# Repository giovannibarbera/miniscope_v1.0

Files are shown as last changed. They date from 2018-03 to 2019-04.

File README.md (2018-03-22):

# MiniScope v1.0 - First generation miniature epifluorescence microscope

This repository contains the design files, software and scripts for fabrication and use of the first generation miniature epifluorescence microscope used in [1] and [2].

## Table of content

[MATLAB-data-analysis](./MATLAB-data-analysis/) - Matlab scripts for image processing/calcium traces extraction

[NeuView](./NeuView/) - Data acquisition software

[PCB-DAQ](./PCB-DAQ/) - Data acquisition PCB design (gerber) files

[PCB-miniscope](./PCB-miniscope/) - MiniScope PCB design (gerber) files

[STL-DAQ](./PCB-miniscope/) - Data acquisition system box

[STL-miniscope](./STL-miniscope/) - MiniScope mechanical design

## References

[1] G. Barbera, B. Liang, L. Zhang, C. R. Gerfen, E. Culurciello, R. Chen, Y. Li, D. Lin. *“Spatially Compact Neural Clusters in the Dorsal Striatum Encode Locomotion Relevant Information”*, Neuron **92**: 1-12, 2016.

[2] L. Zhang, B. Liang, G. Barbera, S. Hawes, Y. Zhang, K. Stump, I. Baum, Y. Yang, Y. Li, D. Lin. *“Miniscope GRIN lens system for calcium imaging of neuronal activity of deep brain structures in behaving animals”*, under review.

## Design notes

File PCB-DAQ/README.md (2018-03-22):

# Data acquisition board design files

The data acquisition system includes:

[CONN_board](../PCB-DAQ/CONN_board/) - Connector board

[DAQ_main_board](../PCB-DAQ/DAQ_main_board/) - Main data acquisition board

[LED_board](../PCB-DAQ/LED_board/) - Indicator LED board

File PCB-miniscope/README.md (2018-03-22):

# MiniScope PCB design files

These are the gerber files for the miniScope PCB. 
Use the text file PCB_specs_MINISCOPE.docx as a reference for the board specification when ordering.

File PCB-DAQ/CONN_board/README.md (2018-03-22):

# DAQ connector board design files

These are the gerber files for the data acquisition connector board. Use the text file PCB_specs_CONN.docx as a reference for the board specification and CONN (Component positions).csv as a placement file when ordering.

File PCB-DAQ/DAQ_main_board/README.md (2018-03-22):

# Data acquisition board design files

These are the gerber files for the data acquisition system. Use the text file PCB_specs_DAQ.docx as a reference for the board specification and DAQ (Component positions).csv as a placement file when ordering.
This DAQ supports dual LED and is wi-fi ready through the TI CC3000 module.

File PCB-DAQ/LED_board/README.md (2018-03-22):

# LED indicator board design files

These are the gerber files for the data acquisition LED indicator board. Use the text file PCB_specs_LED.docx as a reference for the board specification and LED (Component positions).csv as a placement file when ordering.

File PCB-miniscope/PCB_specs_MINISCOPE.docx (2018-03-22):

# PCB specifications for MiniScope v1.0 image sensor board

# Layer order:

1 - Top

Inner 2 - VDD3V3 Plane (POWER)

Inner 3 - DGND Plane (GROUND)

4 - Bottom

# Gerber files description:

# Board Outline: MINISCOPE - Board Outline.gbr

# Bottom Solder Paste: MINISCOPE - Bottom Copper (Paste).gbr

# Bottom Layer: MINISCOPE - Bottom Copper.gbr

Inner Layer 2: MINISCOPE - VDD_3V3 Plane (Powerplane).gbr

Drills: MINISCOPE - Drill Data - [Through Hole].drl

Top Solder Paste: MINISCOPE - Top Copper (Paste).gbr

Top Layer: MINISCOPE - Top Copper.gbr

Top Silkscreen: MINISCOPE - Top Silkscreen.gbr

Bottom Silkscreen: MINISCOPE - Bottom Silkscreen.gbr

Inner Layer 3: MINISCOPE - DGND Plane (Powerplane).gbr

# PCB specifications:

# Layers: 4

PCB Fabrication Spec (IPC Spec): IPC-600G Class 2

Material: Nan Ya NP-175

Finished Thickness: 0.031 inches

Thickness Tolerance: Plus or Minus 10%

Surface Finish: ENIG/HASL

Surface Finish 2: None

Gold Fingers: No

Outer Layer Finish Copper: 1 Oz

Inner Copper: 1 Oz Inners

Flex Board: No

ITAR: No

Board Dimensions: 0.4405 in x 0.4115 in

Route and Retain: No

Scoring : No

ROHS compliant: No

Edge Plating: No

Minimum Hole Size: 19.7 Mils

Minimum Annular Ring Width (Component Holes): 8 mil or more

Internal Slots: None

Internal Cutouts: None

Counter Sink: No

Counter Bore: No

Edge Plated Holes: No

Min Trace (Outer layer): 6 mils

Min Space (Outer layer): 5 mils

Min Trace (Inner layer): 6 mils

Min Space (Inner layer): 5 mils

Solder Mask Sides: Top and Bottom

Solder Mask Via Opens: Covered on both sides

Silk Screen Sides: Both

Thru-Hole Via in Pad: Yes

Thru-Hole Filled Via: Non-Conductive

SM Plugged Vias: No

Minimum Drill to Copper distance: 0.0081 inches

Blind vias: No

Buried vias: No

Controlled depth drilling: No

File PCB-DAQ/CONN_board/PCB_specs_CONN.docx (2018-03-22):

# PCB specifications for MiniScope v1.0 DAQ connector board

# Layer order:

1 - Top

Inner 2 - DGND Plane (GROUND)

Inner 3 - VDD3V3 Plane (POWER)

4 - Bottom

# Gerber files description:

# Board Outline: CONN - Board Outline.gbr

# Bottom Solder Paste: CONN - Bottom Copper (Paste).gbr

# Bottom Solder Mask CONN - Bottom Copper (Resist).gbr

# Bottom Layer: CONN - Bottom Copper.gbr

Bottom Silkscreen: CONN - Bottom Silkscreen.gbr

Inner Layer 2: CONN - DGND Plane (Powerplane).gbr

Drills: CONN - Drill Data - [Through Hole].drl

Top Solder Paste: CONN - Top Copper (Paste).gbr

# Top Solder Mask CONN - Top Copper (Resist).gbr

Top Layer: CONN - Top Copper.gbr

Top Silkscreen: CONN - Top Silkscreen.gbr

Inner Layer 3: CONN - VDD_3V3 Plane (Powerplane).gbr

# PCB specifications:

# Layers: 4

ITAR: no

Certs: IPC Class 2-A600

AS9100: no

Electrical Test: no

5% OVERAGE: no

Material Type: FR4

Material Thickness: 0.062"

Board Finish: LFSolder

Unit Dimensions: 2.2 in x 0.4 in

Tab Rout: no

Scoring: no

Copper Weight: 1 oz

Inner Copper Weight: 1.0

Solder Mask Sides: Both Sides

Solder Mask Color: Green

Legend Silk Scrn: Both Sides

Legd/Silk Scrn Color: White

Castellated Holes: no

Blind/Buried Vias: None

SM Plugged Via: no

Via-In-Pad: None

Microvias: None

Plated Slots: no

Plated Edges: no

CounterSinks: no

CounterBores: no

CtrSinksPlated: 0

CtrBoresPlated: 0

CtrSinksNon-Pltd: 0

CtrBoresNon-Pltd: 0

Ctrld Dielectric: no

Ctrld Impedance: no

Etchback: no

# Pem Nuts: 0

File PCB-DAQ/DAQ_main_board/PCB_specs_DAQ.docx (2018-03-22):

# PCB specifications for MiniScope v1.0 data acquisition board

# Layer order:

1 - Top

Inner 2 - DGND Plane (GROUND)

Inner 3 - VDD3V3 Plane (POWER)

4 - Bottom

# Gerber files description:

# Board Outline: DAQ - Board Outline.gbr

# Bottom Solder Paste: DAQ - Bottom Copper (Paste).gbr

# Bottom Solder Mask DAQ - Bottom Copper (Resist).gbr

# Bottom Layer: DAQ - Bottom Copper.gbr

Bottom Silkscreen: DAQ - Bottom Silkscreen.gbr

Inner Layer 2: DAQ - DGND Plane (Powerplane).gbr

Drills: DAQ - Drill Data - [Through Hole].drl

Top Solder Paste: DAQ - Top Copper (Paste).gbr

# Top Solder Mask DAQ - Top Copper (Resist).gbr

Top Layer: DAQ - Top Copper.gbr

Top Silkscreen: DAQ - Top Silkscreen.gbr

Inner Layer 3: DAQ - VDD_3V3 Plane (Powerplane).gbr

# PCB specifications:

# Layers: 4

ITAR: no

Certs: IPC Class 2-A600

AS9100: no

Electrical Test: no

5% OVERAGE: no

Material Type: FR4

Material Thickness: 0.062"

Board Finish: LFSolder

Unit Dimensions: 2.3 in x 2.1 in

Tab Rout: no

Scoring: no

Copper Weight: 1 oz

Inner Copper Weight: 1.0

Solder Mask Sides: Both Sides

Solder Mask Color: Green

Legend Silk Scrn: Both Sides

Legd/Silk Scrn Color: White

Castellated Holes: no

Blind/Buried Vias: None

SM Plugged Via: no

Via-In-Pad: None

Microvias: None

Plated Slots: no

Plated Edges: no

CounterSinks: no

CounterBores: no

CtrSinksPlated: 0

CtrBoresPlated: 0

CtrSinksNon-Pltd: 0

CtrBoresNon-Pltd: 0

Ctrld Dielectric: no

Ctrld Impedance: no

Etchback: no

# Pem Nuts: 0

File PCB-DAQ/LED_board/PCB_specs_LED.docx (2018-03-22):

# PCB specifications for MiniScope v1.0 DAQ LED board

# Layer order:

1 - Top

Inner 2 - DGND Plane (GROUND)

Inner 3 - DGND Plane2 (GROUND)

4 - Bottom

# Gerber files description:

# Board Outline: LED - Board Outline.gbr

# Bottom Solder Paste: LED - Bottom Copper (Paste).gbr

# Bottom Solder Mask LED - Bottom Copper (Resist).gbr

# Bottom Layer: LED - Bottom Copper.gbr

Bottom Silkscreen: LED - Bottom Silkscreen.gbr

Inner Layer 2: LED - DGND Plane (Powerplane).gbr

Inner Layer 3: LED - DGND Plane2 (Powerplane).gbr

Drills: LED - Drill Data - [Through Hole].drl

Top Solder Paste: LED - Top Copper (Paste).gbr

# Top Solder Mask LED - Top Copper (Resist).gbr

Top Layer: LED - Top Copper.gbr

Top Silkscreen: LED - Top Silkscreen.gbr

Inner Layer 3: LED - VDD_3V3 Plane (Powerplane).gbr

# PCB specifications:

# Layers: 4

ITAR: no

Certs: IPC Class 2-A600

AS9100: no

Electrical Test: no

5% OVERAGE: no

Material Type: FR4

Material Thickness: 0.062"

Board Finish: LFSolder

Unit Dimensions: 0.95 in x 0.36 in

Tab Rout: no

Scoring: no

Copper Weight: 1 oz

Inner Copper Weight: 1.0

Solder Mask Sides: Both Sides

Solder Mask Color: Green

Legend Silk Scrn: Both Sides

Legd/Silk Scrn Color: White

Castellated Holes: no

Blind/Buried Vias: None

SM Plugged Via: no

Via-In-Pad: None

Microvias: None

Plated Slots: no

Plated Edges: no

CounterSinks: no

CounterBores: no

CtrSinksPlated: 0

CtrBoresPlated: 0

CtrSinksNon-Pltd: 0

CtrBoresNon-Pltd: 0

Ctrld Dielectric: no

Ctrld Impedance: no

Etchback: no

# Pem Nuts: 0

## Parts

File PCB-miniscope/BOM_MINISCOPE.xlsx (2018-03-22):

Description | QTY | Ref Des | Manufacturer | Manufacturer PN | Distributor | Distributor PN | Unit price | Ext. price
Ferrite Chip 120Ohm 60mA 0603 | 2 | FERR, FERR1 | TDK | MMZ1608B121C | Digikey | 445-2164-1-ND | $0.100 | $0.200
Cap Cer 1000pF 6.3V X5R 01005 | 1 | C4 | TDK | C0402X5R0J102K020BC | Digikey | 445-5509-1-ND | $0.240 | $0.240
Cap Cer 10000pF 6.3V X5R 01005 | 2 | C6, C12 | TDK | C0402X5R0J103K020BC | Digikey | 445-5515-1-ND | $0.250 | $0.500
Cap Cer 0.1uF 4V 20% X5R 01005 | 3 | C3, C7, C13 | TDK | C0402X5R0G104M020BC | Digikey | 445-8916-1-ND | $0.390 | $1.170
Cap Cer 1uF 6.3V 20% X5R 0201 | 3 | C2, C9, C10 | TDK | C0603X5R0J105M030BC | Digikey | 445-8008-1-ND | $0.370 | $1.110
Cap Cer 10uF 6.3V 20% X5R 0J106 | 3 | C1, C5, C11 | TDK | C1005X5R0J106M050BC | Digikey | 445-8920-1-ND | $0.610 | $1.830
Cap Cer 22uF 6.3V 20% X5R0805 | 1 | C8 | TDK | C2012X5R0J226M125AC | Digikey | 445-1422-1-ND | $0.290 | $0.290
Res 1K OHM 1/32W 5% 01005 SMD | 2 | R1, R2 | Panasonic | ERJ-XGNJ102Y | Digikey | P1.0KAWCT-ND | $0.590 | $1.180
Res 1.5K OHM 1/32W 5% 01005 SMD | 2 | R3, R4 | Panasonic | ERJ-XGNJ152Y | Digikey | P1.5KAWCT-ND | $0.590 | $1.180
Res 220 OHM 1/32W 5% 01005 SMD | 1 | R5 | Panasonic | ERJ-XGNJ221Y | Digikey | P220AWCT-ND | $0.590 | $0.590
IC REG LDO 3.3V 0.5A TSOT23-5 | 1 | ADP1710_3V3 | ON Semiconductors | CAT6219-330TDGT3 | Digikey | CAT6219-330TDGT3CT-ND | $0.970 | $0.970
Polarized Nano Connector PZN-10-VV | 1 | U$1 | Omnetics | A79617-001 | Omnetics | A79617-001 | $27.720 | $27.720
Image Sensor Monochrome CMOS 52-Pin IBGA | 1 | MT9V022 | Aptina | MT9V022IA7ATM | Arrow | MT9V022IA7ATM | $19.070 | $19.070
Tot. |  |  |  |  |  |  |  | $56.050

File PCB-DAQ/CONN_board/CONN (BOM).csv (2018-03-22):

Ref Name | Qty | Component | Value | Side | Manufacturer | Manufacturer part number | Distributor | Distributor part number | Description | Price | Ext price
TRIG LED | 2 | CONN2_THROUGH_2MM |  | Top | Harwin | M80-8520242 | Digikey | 952-1769-ND | 02 SIL MALE CONNECTOR | 1.19 | 2.38
CONN10 | 1 | CONN10_THROUGH_2MM |  | Top | Harwin | M80-8691022 | Digikey | 952-2405-5-ND | CONN HDR 2MM VERT DUAL 10POS | 2.67 | 2.67
CONN25 | 1 | CONN25_FLAT_2013928-8 |  | Bottom | TE Connectivity | 2013928-8 | Digikey | A100213CT-ND | CONN FPC 25POS .3MM FLIP LOC SMD | 1.27 | 1.27
OMNV10 | 1 | OMNETICS_PNZ_10_VV_SMT |  | Top | Omnetics | A79617-001 | Omnetics | A79617-001 | OMNETICS PZN-10-VV | 29 | 29
 |  |  |  |  |  |  |  |  |  | Tot. | 35.32

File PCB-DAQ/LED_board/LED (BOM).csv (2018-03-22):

Ref Name | Qty | Component | Value | Side | Manufacturer | Manufacturer part number | Distributor | Distributor part number | Description | Price | Ext price
LED1 | 1 | LED_GREEN_0805 |  | Top | Lite-On | LTST-C171GKT | Digikey | 160-1423-1-ND | LED GREEN CLEAR THIN 0805 SMD | 0.3 | 0.3
LED2 LED3 LED4 | 3 | LED_BLUE_0805 |  | Top | Lite-On | LTST-C171TBKT | Digikey | 160-1645-1-ND | LED 468NM BLUE CLEAR 0805 SMD | 0.44 | 1.32
U1 | 1 | Molex_0908140906 |  | Bottom | Molex | 908140906 | Digikey | WM3638CT-ND | CONN HEADER 6POS 1.27MM VERT SMD | 1.16 | 1.16
 |  |  |  |  |  |  |  |  |  | Tot. | 2.78

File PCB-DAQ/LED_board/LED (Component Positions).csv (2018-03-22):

Name | Component | Side | Centre X | Centre Y | Rotation
LED2 | LED_BLUE_0805 | Top | 1.72 | -3.46 | 0.00
LED3 | LED_BLUE_0805 | Top | 14.72 | -3.46 | 0.00
LED4 | LED_BLUE_0805 | Top | 21.22 | -3.46 | 0.00
LED1 | LED_GREEN_0805 | Top | 8.22 | -3.46 | 0.00
U1 | Molex_0908140906 | Bottom | 11.78 | -4.51 | 0.00

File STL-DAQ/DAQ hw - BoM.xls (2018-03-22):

DAQ hardware for MiniScope v1.0
Ref Name | Qty | Component | Value | Layer | Manufacturer | Manufacturer PN | Distributor | Distributor PN | Description | Unit price | Ext. Price
* | 1 |  |  | * | Molex | 923150607 | Digikey | WM9492-ND | 6 CKT PICOFLEX 70 MM LONG | $0.68 | $0.68
* | 1 |  |  | * | Molex | 150150425 | Digikey | WM6667-ND | CABLE FLAT FLEX 25POS .30MM 4" | $2.67 | $2.67
* | 1 |  |  | * | Triad Magnetics | WSU050-3000 | Digikey | 237-1387-ND | PWR SUPPLY WALL 5V 3A | $11.34 | $11.34
* | 1 |  |  | * | McMaster | 25995A163 | McMaster | 25995A163 | Bottoming hand tap #2-56 | $5.59 | $5.59
* | 1 |  |  | * | McMaster | 91772A077 | McMaster | 91772A077 | #2-56 pan machine screws 1/4'' (x100) | $4.49 | $4.49
* | 1 |  |  | * | McMaster | 96640A023 | McMaster | 96640A023 | #2-56 flat machine screws 1/4'' (x100) | $3.84 | $3.84
* | 56 |  |  | * | 3M | SJ-5012 (BLACK) | Digikey | SJ5012-0-ND | BUMPON CYLINDRICAL .50X.14 BLACK | $0.07 | $3.79
* | 1 |  |  | * | Opal Kelly | XEM3010-1000 | Opal Kelly | XEM3010-1000 | FPGA board | $399.95 | $399.95
Tot. | 63 |  |  |  |  |  |  |  |  |  | $432.35
*Not mounted on PCB

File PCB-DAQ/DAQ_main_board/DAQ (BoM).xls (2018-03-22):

DAQ - MiniScope v1.0
Ref Name | Qty | Component | Value | Layer | Manufacturer | Manufacturer PN | Distributor | Distributor PN | Description | Unit price | Ext. Price
AD7091 | 1 | AD7091 |  | Bottom | Analog Devices | AD7091BCPZ-RL7 | Digikey | AD7091BCPZ-RL7CT-ND | IC ADC 12BIT SPI/SRL 1M 8-LFSCP | $4.15 | $4.15
AD7398 | 1 | AD7398 |  | Bottom | Analog Devices | AD7398 | Digikey | AD7398BRUZ | IC DAC 12BIT QUAD SRL-IN 16TSSOP | $19.48 | $19.48
U4 | 1 | ANTENNA |  | Top | Johanson | 2450AT43B100E | Digikey | 712-1010-1-ND | ANTENNA CHIP 2.4GHZ | $1.01 | $1.01
JP2, JP3 | 2 | BTE-040-01-F-D-A |  | Bottom | Samtec | BTE-040-01-L-D-A | Digkey | SAM8745-ND | CONN HEADER 40POS .031" SMT GLD | $6.53 | $13.06
C16 | 1 | C0201_0.3p_25V | .3p | Bottom | Johanson | 250R05L0R3AV4T | Digikey | 712-1174-1-ND | CAP CER 0.3PF 25V NP0 0201 | $0.12 | $0.12
C9, C11, C15, C17, C2 | 5 | C0402_0.1u_16V | .1u | Top, Bottom | Murata | GRM155R71C104KA88D | Digikey | 490-3261-1-ND | CAP CER 0.1UF 16V 10% X7R 0402 | $0.10 | $0.50
C10, C12, C22, C23, C25 | 5 | C0402_1n_50V | 1n | Top, Bottom | Murata | GRM155R71H102KA01D | Digikey | 490-1303-1-ND | CAP CER 1000PF 50V 10% X7R 0402 | $0.10 | $0.50
C3, C6, C18, C21, C24, C26 | 6 | C0402_1u_16V | 1u | Top, Bottom | Murata | GRM155R60J105ME19D | Digikey | 490-1319-1-ND | CAP CER 1UF 6.3V 20% X5R 0402 | $0.10 | $0.60
C4, C7 | 2 | C0402_2.2u_4V | 2.2u | Top, Bottom | Murata | GRM155R60G225ME15D | Digikey | 490-4518-1-ND | CAP CER 2.2UF 4V 20% X5R 0402 | $0.27 | $0.54
C20 | 1 | C0402_4.7n_25V | 4.7n | Bottom | Murata | GRM155R71E472KA01D | Digikey | 490-1309-1-ND | CAP CER 4700PF 25V 10% X7R 0402 | $0.10 | $0.10
C5, C8, C14 | 3 | C0402_10n_25V | 10n | Top | Murata | GRM155R71E103KA01D | Digikey | 490-1312-1-ND | CAP CER 10000PF 25V 10% X7R 0402 | $0.10 | $0.30
C1, C19 | 2 | C0603_10u_6.3V | 10u | Bottom | Murata | GRM188R60J106ME47D | Digikey | 490-3896-1-ND | CAP CER 10UF 6.3V 20% X5R 0603 | $0.27 | $0.54
C13 | 1 | C0805_22u_6.3V | 22u | Top | Murata | GRM21BR60J226ME39L | Digikey | 490-1719-1-ND | CAP CER 22UF 6.3V 20% X5R 0805 | $0.29 | $0.29
U2, U3 | 2 | CAT6219_3V3 |  | Top | ON Semiconductor | CAT6219-330TDGT3 | Digikey | CAT6219-330TDGT3CT-ND | IC REG LDO 3.3V 0.5A TSOT23-5 | $0.97 | $1.94
CC3000 | 1 | CC3000 |  | Top | TI | CC3000MOD | Digikey | 296-35057-ND | MOD SIMPLELINK WI-FI CC3000 | $14.49 | $14.49
CAM | 1 | CONN25_FLAT_2013928-8 |  | Top | TE Connectivity | 2013928-8 | Digikey | A100213CT-ND | CONN FPC 25POS .3MM FLIP LOC SMD | $1.27 | $1.27
DS93 | 1 | DS92LV1212A |  | Bottom | TI | DS92LV1212AMSA | Digikey | DS92LV1212AMSA-ND | IC DESERIALIZER 10-BIT 28-SSOP | $8.21 | $8.21
FERR | 1 | FERR | 120 | Top | TDK | MMZ1608B121C | Digikey | 445-2164-1-ND | FERRITE CHIP 120 OHM 600MA 0603 | $0.10 | $0.10
U1, U6 | 2 | IRLML2060 |  | Top | International Rectifier | IRLML2060TRPBF | Digikey | IRLML2060TRPBFCT-ND | MOSFET N-CH 60V 1.2A SOT23-3 | $0.36 | $0.72
L7, L8 | 2 | L0402_1.0NH | 1.0nH | Bottom | Murata | LQG15HN1N0S02D | Digikey | 490-1073-1-ND | INDUCTOR 1.0NH 300MA 0402 | $0.10 | $0.20
L6 | 1 | L0402_2.2NH | 2.2nH | Top | Johanson | L-07C2N2SV6T | Digikey | 712-1414-1-ND | CER INDUCTOR 2.2NH 0402 | $0.10 | $0.10
L5 | 1 | L0402_2.7NH | 2.7nH | Top | Johanson | L-07C2N7SV6T | Digikey | 712-1415-1-ND | CER INDUCTOR 2.7NH 0402 | $0.10 | $0.10
LED | 1 | Molex_0908140906 |  | Top | Molex | 908140906 | Digikey | WM3638CT-ND | CONN HEADER 6POS 1.27MM VERT SMD | $1.16 | $1.16
R17, R18, R19, R20, R21, R22, R23, R24, R25, R26, R27, R28, R11 | 13 | R0201_0_1/20 | 0 | Top, Bottom | Vishay Dale | CRCW02010000Z0ED | Digikey | 541-0.0AGCT-ND | RES 0.0 OHM 1/20W JUMP 0201 SMD | $0.13 | $1.69
R15, R16 | 2 | R0603_0_1/10 | 0 | Bottom | Vishay Dale | RCG06030000Z0EA | Digikey | 541-1888-1-ND | RES 0.0 OHM 1/10W JUMP 0603 SMD | $0.10 | $0.20
R9, R13 | 2 | R0603_10k_1/10 | 10k | Top | Panasonic | ERJ-3GEYJ103V | Digikey | P10KGCT-ND | RES 10K OHM 1/10W 5% 0603 SMD | $0.10 | $0.20
R10, R1, R2, R3, R4, R8, R12 | 7 | R0603_51_1/10 | 51 | Bottom | Panasonic | ERJ-3EKF51R0V | Digikey | P51.0HCT-ND | RES 51 OHM 1/10W 1% 0603 SMD | $0.10 | $0.70
R6 | 1 | R0603_1470k_1/10 | 1.47k | Top | Panasonic | ERJ-3EKF1471V | Digikey | P1.47KHCT-ND | RES 1.47K OHM 1/10W 1% 0603 SMD | $0.10 | $0.10
RS1, RS2, RS3, RS4, RS5, RS6, RS7, RS8 | 8 | R1206_10_1/4 | 10 | Top | Vishay Dale | RCG120610R0FKEA | Digikey | 541-1851-1-ND | RES 10 OHM 1/4W 1% 1206 SMD | $0.12 | $0.96
Tot. | 77 |  |  |  |  |  |  |  |  |  | $73.33

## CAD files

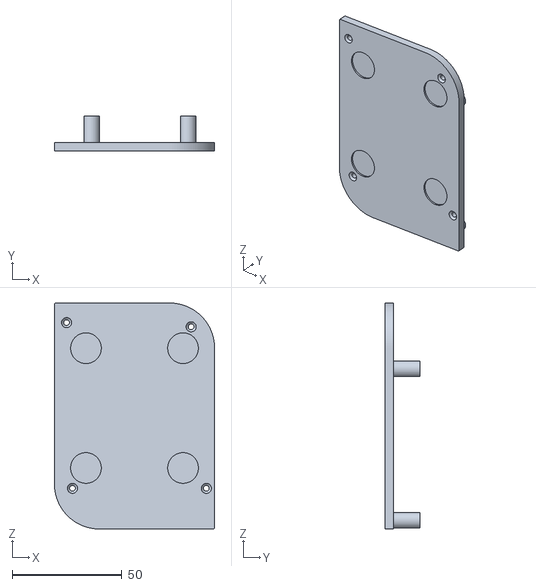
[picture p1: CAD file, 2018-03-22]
STL-DAQ/bottom.STL
73.0 x 16.0 x 103.0

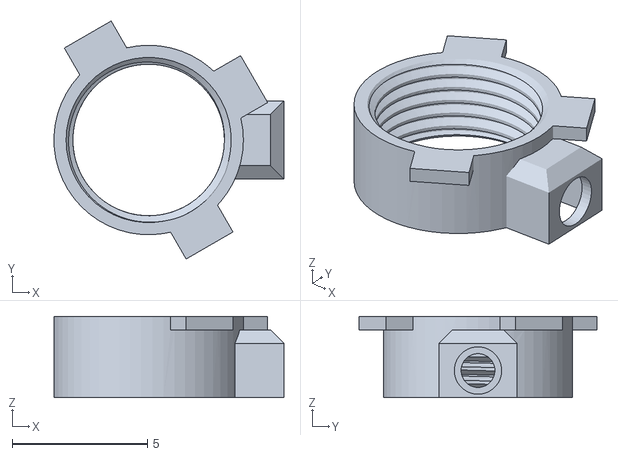
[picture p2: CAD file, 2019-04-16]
STL-miniscope/2_Bottom.STL
8.50 x 8.79 x 3.00

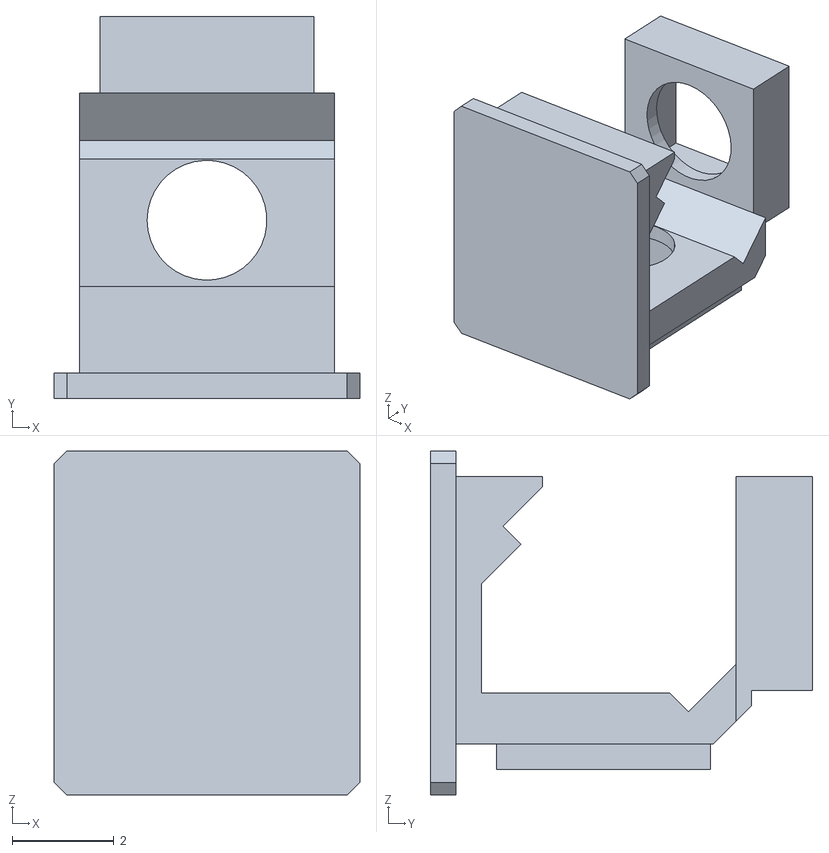
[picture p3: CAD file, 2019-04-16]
STL-miniscope/3_FilterCube.STL
6.00 x 7.50 x 6.75

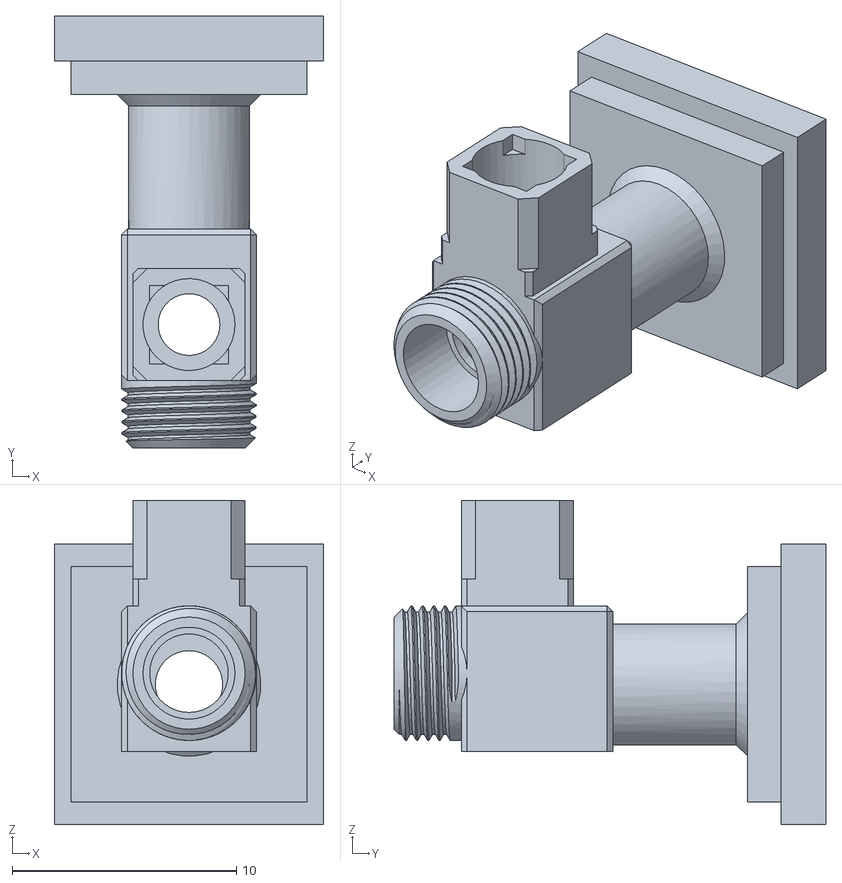
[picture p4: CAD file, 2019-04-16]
STL-miniscope/1_Housing.STL
12.0 x 19.2 x 14.5
